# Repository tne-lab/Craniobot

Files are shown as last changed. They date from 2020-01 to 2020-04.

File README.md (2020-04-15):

# "Craniobot", a craniotomy robot for small rodents.
This is a simple 3-axis high-prcision robot designed to perform craniotomies on small rodents. 
These small craniotomies are often needed for electrode implantation and neuroscience research.
Control of the robot is done using CraniobotGUI2.5.py user interface. Drill_holes2.py and drill_craniotomy2.py are called by the GUI. Some ThorLabs control functions are included in the throlabs_apt_master folder. The RESOURCES folder contains GUI elements, logos, and graphics. 

## General Description
The robot consists of three ThorLabs 2.5 cm linear actuators, 
a 3D printed streotaxi alignment tool, a 3D printed drill holder, some mounting hardware, 
and a python GUI interface developed by Flavio JK da Silva and Mark Scatza along with a craniotomy layout tool by Flavio.  The 3D printed parts were designed using FreeCAD.  
The *.stl files as well as the FreeCAD files are available here in the PARTS folder.

## GUI interface
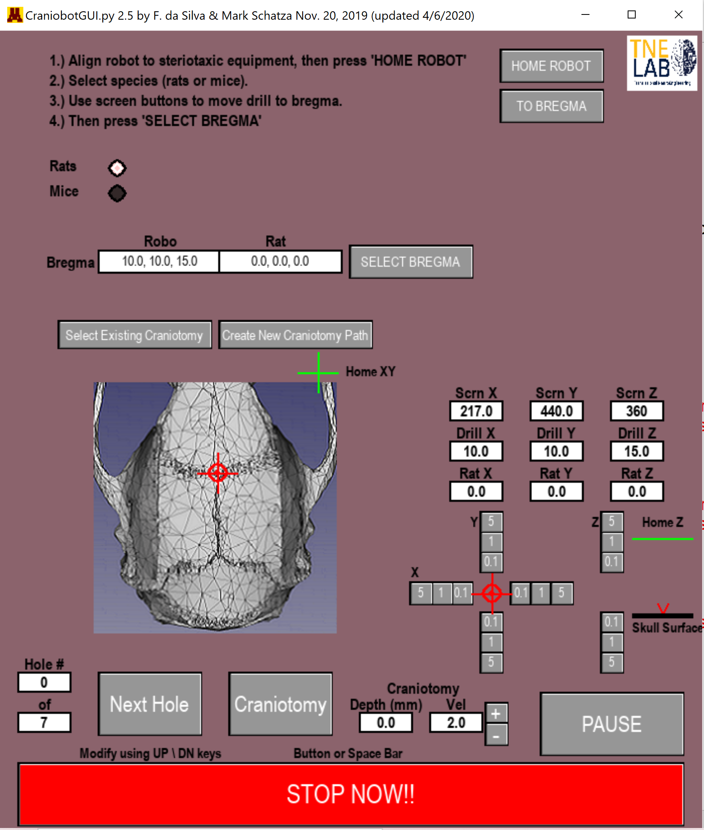
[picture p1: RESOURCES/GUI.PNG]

Control of the robot is done using setupGUI2.0.py. Drill_holes2.py and drill_craniotomy.py are called by the GUI. 
Some ThorLabs control functions are included in the throlabs_apt_master folder. The RESOURCES folder contains GUI elements, logos, and graphics. After the skull is surgically exposed,  The robot is pushed against the stereotaxic equipment to align the XY plane of the robot with the XY plane of the sterotaxic equipment.
Then use the XYZ motion control buttons to move the drill to the rodent (0,0,0) point (the Bregma location) to establish a point of correspondance between the robot and rodent coordinates.  
It is assumed that the surface of the skull is horizontal. The surface of the skull easily oriented along a horizontal plane using stereotaxic equipment and a trident alignment tool.  
The GUI displays the drill current position, as well a record of where cuts have been made.  Each pass of the craniotomy is only 0.1 mm deep.  
After each pass the user has the option of doing another pass, each 0.1 mm deeper.  Screw holes are set to be 1.0 mm deep, but the user has 
the option of going deeper in 0.1 mm increments.  The position of the drill along any axis can be manipulated by the control buttons on the GUI.

## RUNNING THE CRANIOBOT
All necessary Craniobot software is on this GITHUB. To start run CaniobotGUI2.5.py All the commands you need to run the Caniobot are iconified on the screen.
1.	Using the trident stereotaxic leveling tool, be sure the rodent skull is level.
2.	Select Species. Currently only Rats or Mice are available.
3.	Align the Craniobot with the stereotaxic equipment.
This is done by pushing the Craniobot snuggly against the right side of the stereotaxic equipment.
Secure it in place. Taping it down to the table works fine for me. Remember the robot only has a 2.5 cm range of motion along each axis.
It is therefore desirable that the tip of the drill is roughly at the bregma when the robot X,Y,Z is at approximately (12.5 , 12.5, 12.5). Though X,Y,Z = 10, 10, 10 is perfectly adequate for most surgeries.
Best Practice: Home the robot. The use the XYZ buttons to move the robot to approximately X,Y,Z = 10, 10 , 10.
Move the entire robot assembly so that the drill is just above the Bregma.
Note: The drill bit most likely can NOT be inserted entirely into the drill, rather let it stick out about 3 cm so that it just touches the skull when Z is approximately 10 to 20 cm.
4.	When the robot assembly is aligned to the stereotaxic equipment and the robot is approximately in the middle of its working volume (~10, ~10, ~ 10), use the XYZ move buttons to touch the drill precisely to the Bregma.
Then press the SELECT BREGMA button. You should see a red circle and cross-hairs over the bregma graphic.
5.	Select an Existing Craniotomy or Create New Craniotomy Path.
Any pre-existing craniotomy path can be edited using the Craniotomy Designer stand alone application by pressing the Create New Craniotomy Path button.
6.	Be sure drill is ON and going in the FWD direction.
7.	CRANIOTOMY: Press Craniotomy button. One pass of the entire craniotomy path depicted in the screen graphics will be reproduced by the robot.
8.	Repeat Step 5. On each pass, the drill will cut the path 0.1 mm deeper.
Repeat until through skull (approximately 10 passes). NOTE: The craniobot assumes that the rodent skull is level.
9.	SCREW HOLES: Next press Next Hole Button to create screw holes. When the drill stops, used the Z axis motion control button to go deeper if necessary. When drilled to the depth you desire, press the Next Hole button to go to the next hole location

## USING THE CRANIOTOMY DESIGNER 
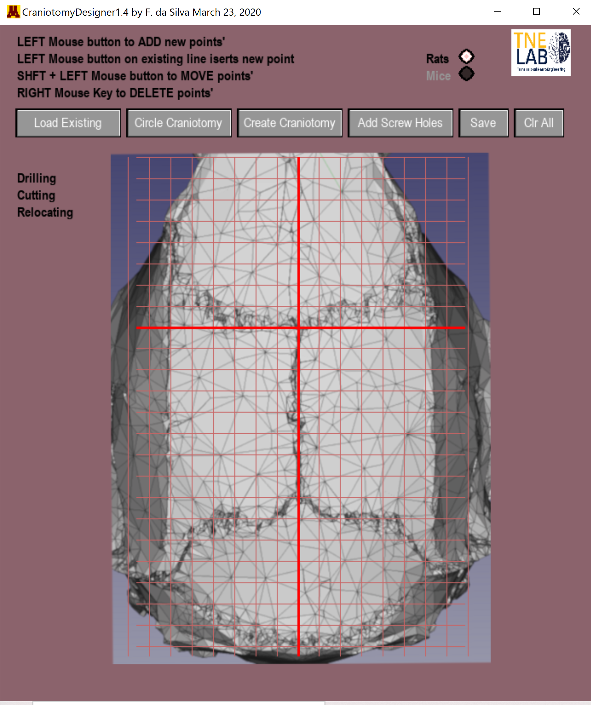
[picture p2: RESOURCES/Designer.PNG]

The Craniotomy Designer is a separate, but fully integrated module that is used to design craniotomy paths for the Craniobot. It can be run as a stand-alone software, or called from the CraniobotGUI application. The GUI should be self explanatory. Click on the button icons to load an existing craniotomy path, create simple circular craniotomies, created complex arbitrary craniotomies, add screw-hole locations, save or clear the screen. As soon as the mouse is dragged over the window, the cursor location (in skull coordinates) appear next to it. Please see the included video for a quick tour: CraniotomyDesigner 1.4 by Flavio...
Making a circular craniotomy: When the circular craniotomy button is pressed, user input boxes appear on the left of the skull graphic. Click on the box, its
outline will turn red, then type the desired values for the radius, and the X and Y offsets from the Bregma. As soon as the last value is entered, a path for the robot to follow will appear on the screen.
To add a point, simply select the create craniotomy button, then simply click anywhere on a blue line. Another point will be added.
To delete a point, left click on any point and it will disappear.
To Move an existing point, hold down the shift key while left clicking on a point, then move it to anywhere on the screen.
Making a craniotomy with an arbitrary path:
To create an arbitrary path, simply click on the Create Craniotomy Button. Using the left mouse button, place points (in red) on the skull graphic. Multiple points will constitute a path along the X and Y axes for the robot to follow. When the path is complete, the resulting closed path will turn blue. Move points by simultaneously holding down the SHIFT key and left clicking on a point. Add points by clicking anywhere on an existing line.
Adding Screw Holes: Simply click on the Add Screw Holes button, then left click the mouse on any point on the skull. The robot will go to that point and drill along the Z-axis.
FINISHING IT UP: When happy with your design, simply press the Save button. All craniotomy patterns are stored in the CRANIOTOMY DESIGNS folder. Now simply run the craniotomy robot, and load your desired path.

## SOFTWARE INTALLATION GUIDE 
1.	Install Python 3.7 or higher. I prefer to install it as stand alone. a. During installation, choose Custom installation. Them place your Python in new folder. I created one called
c:\python3.8.
b. Be sure to Install 64 bit version if your computer is 64 bit c. Be sure to add python to system path when asked.
2.	Install pygame.
a. Type cmd in windows search bar at bottom left of screen b. In the pop-up command window, type: cd .. Enter, then cd .. Enter (yes, do it twice) c. Then cd c:\python3.8 (or whatever directory you used above) d. Then type: pip install pygame
3.	Install numpy. Using CMD prompt as above in 2, type: pip install numpy
4.	Install Thorlabs-apt. Using CMD prompt as above, type: pip install Thorlabs-apt
5.	Install ThorLabs: https://www.thorlabs.com/newgrouppage9.cfm?objectgroup_id=10285 a. Goto Kinessis Software tab, and press the Softwate Download button.
b. choose 64 bit if your computer is 64 bit.
6.	Go to Github and clone the Thorlabs_apt depository. See https://github.com/qpit/thorlabs_apt a. In the download folder, extact all of the download. b. Then run the setup.py program using install as the only argument. c. That is, type: python setup.py install
7.	Copy G:\Shared drives\TNEL - UMN\Project related material\craniobot\APT.dll into the Windows\System32 directory
8.	Copy entire craniobot directory to your desktop. see G:\Shared drives\TNEL - UMN\Project related material\craniobot
9.	Now you should be ready to use the craniobot application. NOTE: Be sure to exit Craniobot using Windows exit “X” on top right of window. If not, all motors will be locked out (that is, already in use). To fix this problem, run Thorlabs Kinesis software. Load all three motors. When all three alre loaded, unload all, then run Carniobot again.

[MAINGUI]: https://github.com/tne-lab/Craniobot/blob/master/RESOURCES/GUI.PNG "GUI" 

[Designer]: https://github.com/tne-lab/Craniobot/blob/master/RESOURCES/Designer.PNG "GUI"

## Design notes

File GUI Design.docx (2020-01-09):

1.) Bite Bar
2.) Ear Bars
3.) Incision (between the eyes to between ears)
4.) Peel back skin using four or more hemostats
5.) Level head using stereotaxic trident
6.) Home robot (to robot 0,0,0)
7.) Center robot drill-tip on rat Bregma (0,0,0) and set. This sets the relationship between the robot coordinates and rat coordinate. It is assumed the coordinate systems are aligned (Xrobo parallet to Xrat, and so on)
8.) This can be displayed on the screen using screen coordinate system
9.) Move robot drill to 4 more points on the skull. This will be used to establish the best fit plane through those points on the skull. The craniotomy circle will be cut on this plane.
10.) Find bet-fit plane using a minimum of 5 points including bregma.
11.) Follow pop-up instructions to operate robot.

Center offset from Bregma

-1.7,0,0

Radius

5

mm

Y

X

Z

Draw Route

Circle

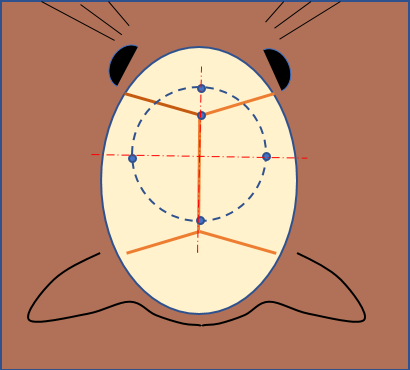
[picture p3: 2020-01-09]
RESOURCES/skull_graphicA.PNG

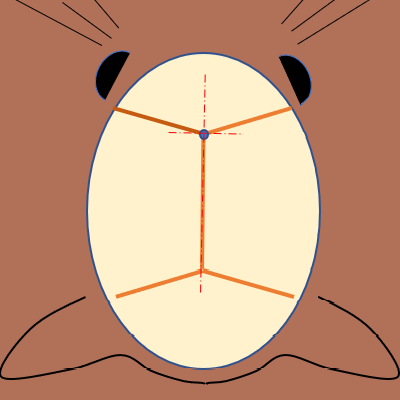
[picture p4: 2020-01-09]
RESOURCES/skull_graphic.PNG

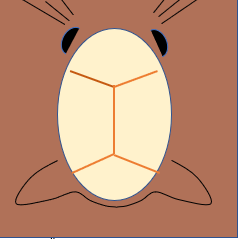
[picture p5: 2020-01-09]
RESOURCES/skull_graphicB.PNG

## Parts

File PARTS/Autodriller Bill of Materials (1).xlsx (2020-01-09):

ITEM # | DESCRIPTION | PART # | VENDOR | COST | QUANTITY | TOTAL COST | WEBLINK/CAD file information
 | MAIN CNC mill apparatus
1 | DIY CNC router kit | B015CJ1OFS | Amazon | $399 | $1 | $399 | https://www.amazon.ca/Konmison-Carving-Milling-Engraving-10000rpm/dp/B015CJ1OFS?s=hi
2 | Arduino Uno | 485-2877 | Mouser | $23.38 | $1.00 | $23.38 | https://www.mouser.com/ProductDetail/Arduino/2877/?qs=OXlZGzED1NaiMhNo5b2aJg%3D%3D
3 | TinyG | TinyG | Syntheos | $139.00 | $1.00 | $139 | https://synthetos.myshopify.com/collections/assembled-electronics/products/tinyg
4 | Power supply for CNC | B07DT62KL8 (or equivalent) | Amazon | $19.73 | 1 | $19.73 | https://www.amazon.com/uxcell-Switch-Supply-Driver-S-120-24/dp/B07DT62KL8
5 | DC power supply for Spindle | B01IHG8D8O (or equivalent) | Amazon | $48.99 | 1 | $48.99 | https://www.amazon.com/dp/B01IHG8D8O
6 | Limit Switches | Z5065-ND | Digikey | $2.62 | 5 | $13.1 | https://www.digikey.com/product-detail/en/omron-electronics-inc-emc-div/SS-10GL-3/Z5065-ND/5236940&
7 | standoffs, 1/2" hex x 1" for mounting electroics board to CNC in the back | 92319A772 | McmasterCarr | $3.48 | 4 | $13.92 | https://www.mcmaster.com/catalog/124/3301
8 | Standoff for mounting TinyG and Arduino | 96110A011 | McmasterCarr | $1.45 | 8 | $11.6 | https://www.mcmaster.com/catalog/124/3363
9 | Electronics Mounting board | Custom designed and laser cut | - | - | - | - | See CAD File "Circuit_Board_Holder.dxf" for details
10 | Sheet metal screws for mounting the stereotax | 92470A123 | McmasterCarr | $8.14 | 1 |  | https://www.mcmaster.com/92470a123
 | Custom Stereotax
1 | TR1.5 0.5" Thorlabs post | TR1.5 | Thorlabs | $4.74 | 3 | $14.22 | https://www.thorlabs.com/NewGroupPage9.cfm?ObjectGroup_ID=1266
2 | TR2 optical post | TR2 | Thorlabs | 5.19 | 3 | $15.57 | https://www.thorlabs.com/NewGroupPage9.cfm?ObjectGroup_ID=1266
3 | Aluminum board for stereotax | Custom Designed |  |  |  |  | See CAD File "base_simple_waterjet.dxf for details
3 | Right angle clamp | RA90 | Thorlabs | $9.76 | 3 | 29.28 | https://www.thorlabs.com/newgrouppage9.cfm?objectgroup_id=1985&pn=RA90#6066
4 | Disposable 3D printed bite bar | Custom designed and 3D printed | - | - | - | - | See CAD File "bite_bar_hex.stl" for details
5 | Disposable 3D printed nose cone | Custom designed and 3D printed | - | - | - | - | See CAD File "anesthesia_mask_hex.stl" for details
6 | 1/4-20 2" long threaded steel rod | 90322A648 | McmasterCarr | $3.76 | 2 | 7.52 | https://www.mcmaster.com/90322a648
6 | Aluminum 0.25" female hex standoff with 8-32 thread | 91115A198 | MCmasterCarr | $2.36 | 1 | 2.36 | https://www.mcmaster.com/hex-standoffs
7 | M3 x 10 mm hex screw | 91292A113 | MCmasterCarr | $4.53 | 1 | 4.53 | https://www.mcmaster.com/socket-head-cap-screws
9 | M3 X 6mm x 5 mm Brass insert | B0784VYCYY | Amazon | $0.25 | 1 | 0.25 | Taken from : https://www.amazon.com/Hilitchi-250-Pcs-Threaded-Embedment-Assortment/dp/B0784VYCYY
 | Low force surface profiler
1 | Tormach profiler | 32310 | Tormach | $229 | $1 | $229 | https://www.tormach.com/product_tts_passive_probe.html
2 | Ruby tip Stylus | TH M2 003 03 010 | Itpstyli | $79 | 1 | $79 | https://www.itpstyli.com/
3 | Low force spring | Custom Designed and waterjet cut | - | - | - | - | See CAD file "Stainless_Spring.dxf" for details
4 | Stylus tip holder | Custom Designed and 3D printed | - | - | - | - | See CAD file "Tip_holder.stl" for details
5 | 1/8" x 0.5" long brass pins (3 nos.) | 97325A135 (Pack of 25) | McmasterCarr | $13.76 | 1 | $1.65 | https://www.mcmaster.com/brass-pins
6 | 0-80 screws 0.5" long (3 nos.) | 92196A070 (Pack of 50) | McmasterCarr | $10.83 | 1 | $1.30 | https://www.mcmaster.com/catalog/124/3196
7 | 4-40 X 0.25" length (3 nos.) | 91772A106 (Pack of 100) | McmasterCarr | $3.39 | 1 | $0.10 | https://www.mcmaster.com/=1f674uq
8 | M4 screws X 5mm long (3 nos.) | 95836A332 (Pack of 50) | McmasterCarr | $11.85 | 1 | $1.42 | https://www.mcmaster.com/pan-head-machine-screws
9 | Acrylic holder for housing the surface probe when not in use | Custom Designed and laser cut |  |  |  |  | See CAD file "profiler holder.dxf" and "profiler holder.sldprt" for details
 |  |  |  |  | TOTAL | $1054.9245
 | List of tools
1 | 4-40 Tap
2 | 1/4- 20 Tap
3 | 2-56 tap
4 | 5/32 tap
5 | 6/32 tap
6 | 8/32 tap
7 | M4 tap
8 | 0-80 tap
9 | M2 tap
10 | Drills
11 | Set of Allen Wrenches
12 | Set of Phillips head screwdriveers
13 | Small Flathead screw drivers for terminals on the Tiny G
14 | Hot glue gun
15 | Sand Paper for sanding the 3D printed parts
16 | Pliers
17 | Scissors
18 | Wires, jumper cables, Breadboard and miscellaneous electronics prototyping tools
19 | Teflon tape
20 | Laboratory weighing scale with resolution of 1g of higher

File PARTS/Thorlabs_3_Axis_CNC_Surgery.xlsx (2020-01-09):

Thorlabs PN | Description | QTY | Price Ea | Price Total
KMTS25E (https://www.thorlabs.com/thorproduct.cfm?partnumber=KMTS25E) | 25 mm (0.98") Motorized Translation Stage Bundled with Controller (KDC 101) and Power Supply, 8-32 and 4-40 Taps | 3 | $1363.23 | $4089.69
MTSA1 (https://www.thorlabs.com/thorproduct.cfm?partnumber=MTSA1) | Adapter Plate with 1/4"-20 and 8-32 Tapped Holes for MTS25 and MTS50 Stages | 1 | $42.84 | $42.84
MTS25B-Z8 (https://www.thorlabs.com/thorproduct.cfm?partnumber=MTS25B-Z8) | XY Adapter Plate for MTS25 Series Translation Stages | 1 | $41.82 | $41.82
MTS25C-Z8 (https://www.thorlabs.com/thorproduct.cfm?partnumber=MTS25C-Z8) | Right-Angle Bracket for MTS25 Series Translation Stages | 1 | $89.76 | $89.76
MTS25A-Z8 (https://www.thorlabs.com/thorproduct.cfm?partnumber=MTS25A-Z8) | Base Plate for MTS25 Series Translation Stages | 1 | $65.28 | $65.28
P14 (https://www.thorlabs.com/thorproduct.cfm?partnumber=P14) | Ø1.5" Mounting Post, 1/4"-20 Taps, L = 14" | 1 | $88.00 | $88.00
C1515 (https://www.thorlabs.com/thorproduct.cfm?partnumber=C1515) | Ø1.5" Mounting Post Bracket, 1/4"-20 Taps | 1 | $97.00 | $97.00
MB6 (https://www.thorlabs.com/thorproduct.cfm?partnumber=MB6) | Aluminum Breadboard 6" x 6" x 1/2", 1/4"-20 Taps | 1 | $48.00 | $48.00
 |  |  | TOTAL: | $4562.39

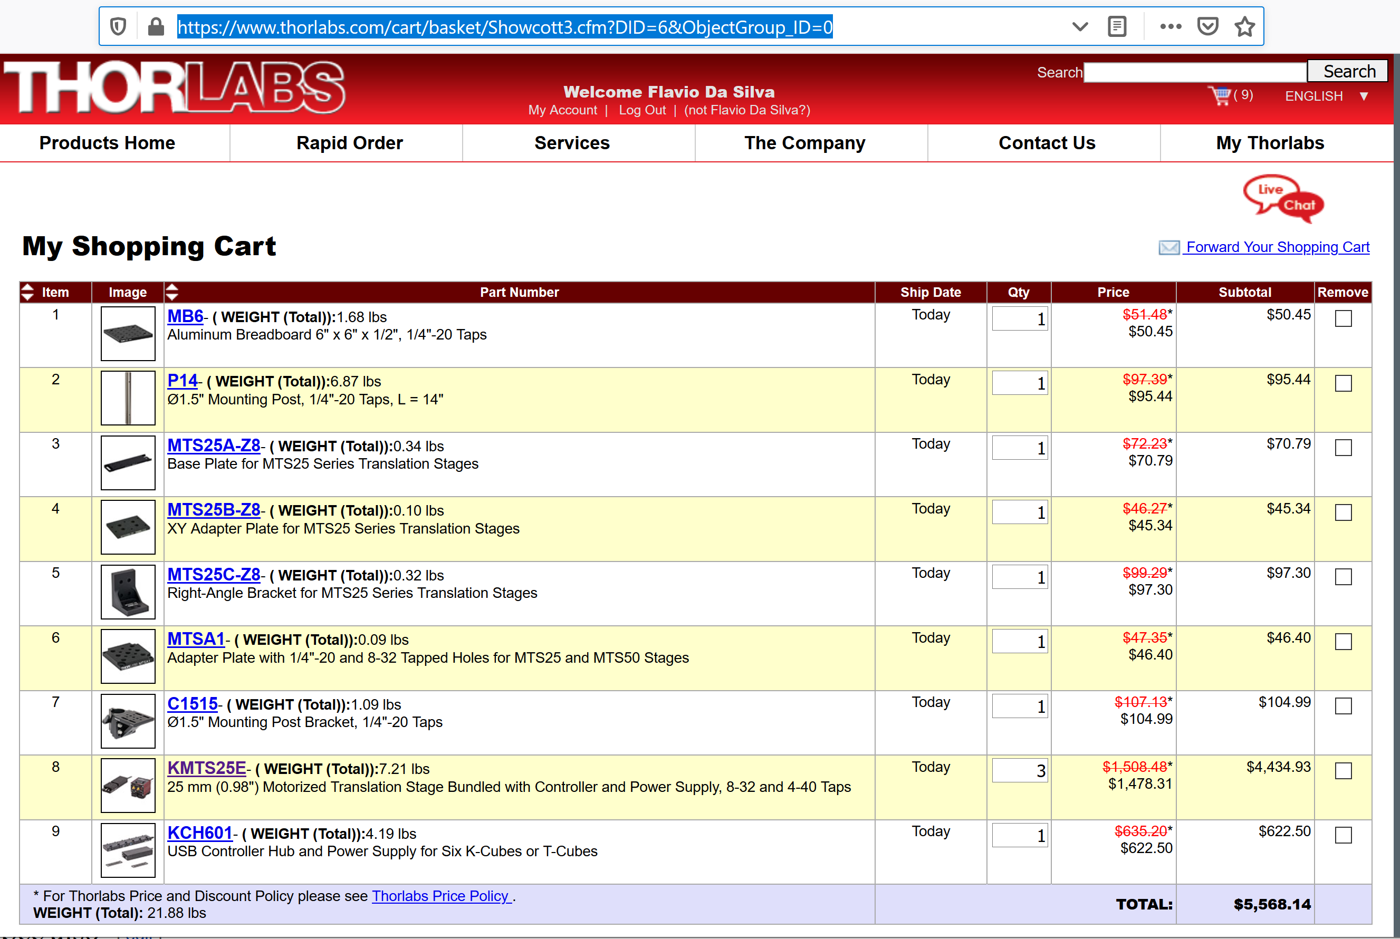
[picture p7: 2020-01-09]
PARTS/partsList.PNG

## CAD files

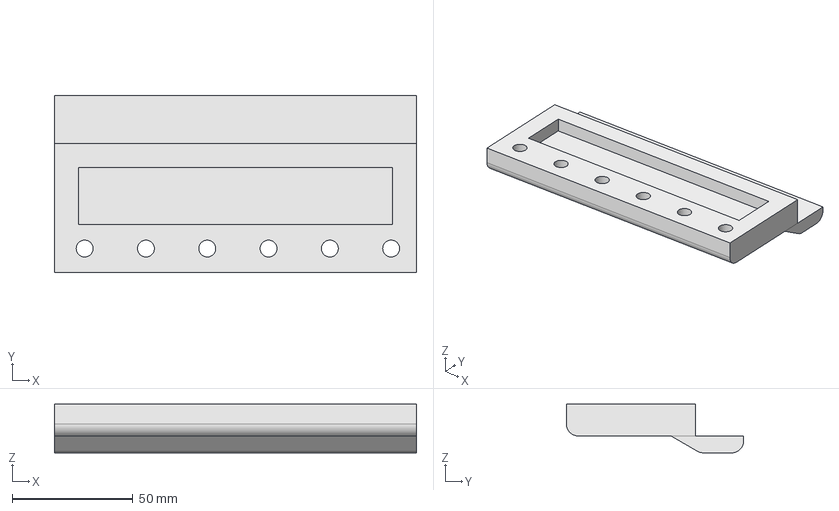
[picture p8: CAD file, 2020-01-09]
PARTS/StereoTaxicAlignmentTool1.FCStd
150.0 x 73.5 x 20.2 mm

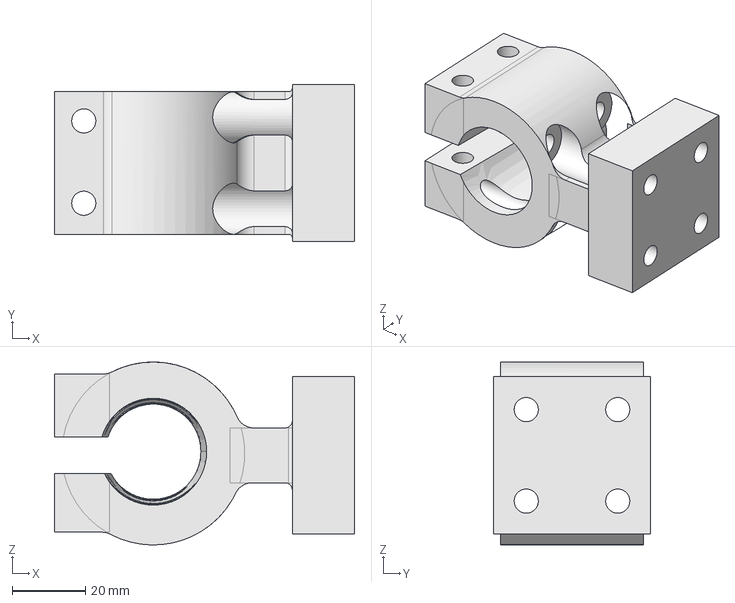
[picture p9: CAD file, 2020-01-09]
PARTS/DrillHolder.FCStd
82.0 x 43.0 x 50.0 mm

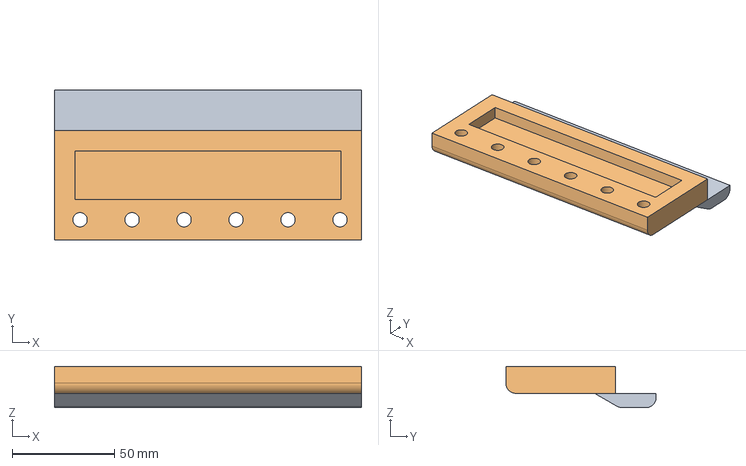
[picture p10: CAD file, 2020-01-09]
PARTS/StereoTaxicAlignmentTool.FCStd
150.0 x 73.5 x 20.2 mm

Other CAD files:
PARTS/DrillHolder.stl
PARTS/StereoTaxicAlignmentTool.stl
